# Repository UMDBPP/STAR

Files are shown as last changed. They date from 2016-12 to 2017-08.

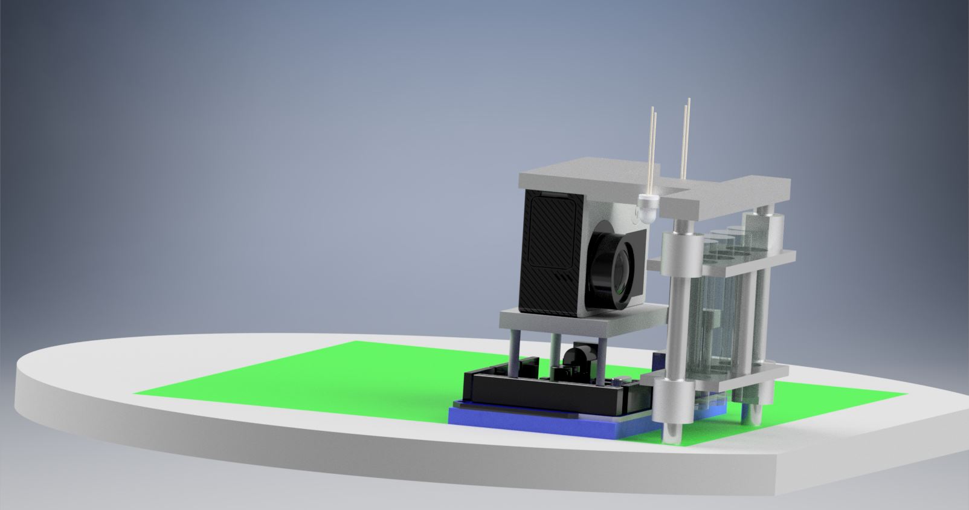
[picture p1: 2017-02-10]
CAD/Mechanical/Renderings and PDFs/Full payload assembly.jpg

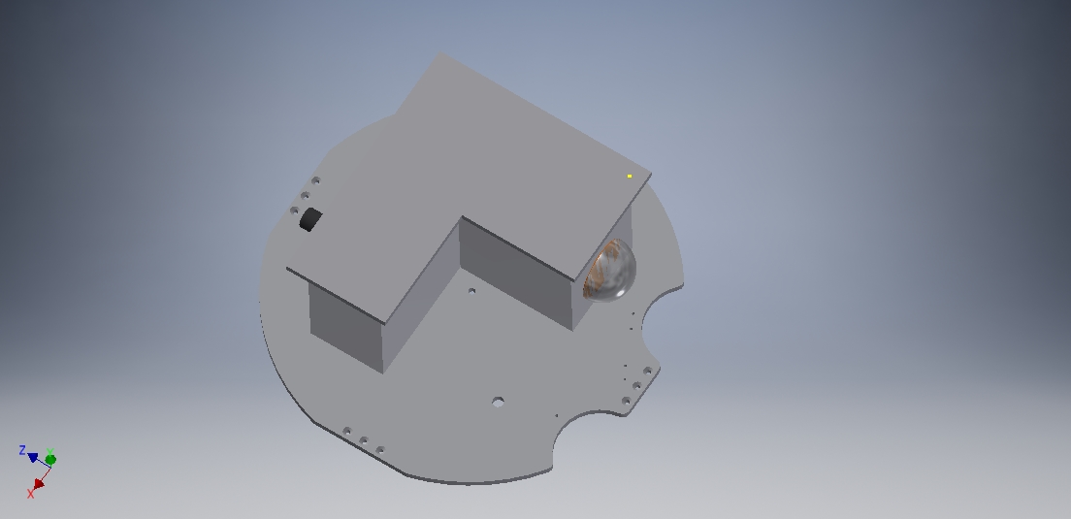
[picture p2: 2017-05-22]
CAD/Mechanical/CapTech/CADD/CADD/RSX Assembly/RSX Assembly.jpg

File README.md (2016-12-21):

# STAR
Sratification and Tribocharging Analysis of Regolith

## Purpose
This is a payload for the 2017 RockSatX project. It's purpose is to provide experimental data for validating a behavioral model proposed by Dr. Christine Hartzell.

The payload will:
* Observe stratification of varying bimodal grain size distribution under microgravity and external excitation
* Measure effect of tribocharging upon spherical non-conducting grains

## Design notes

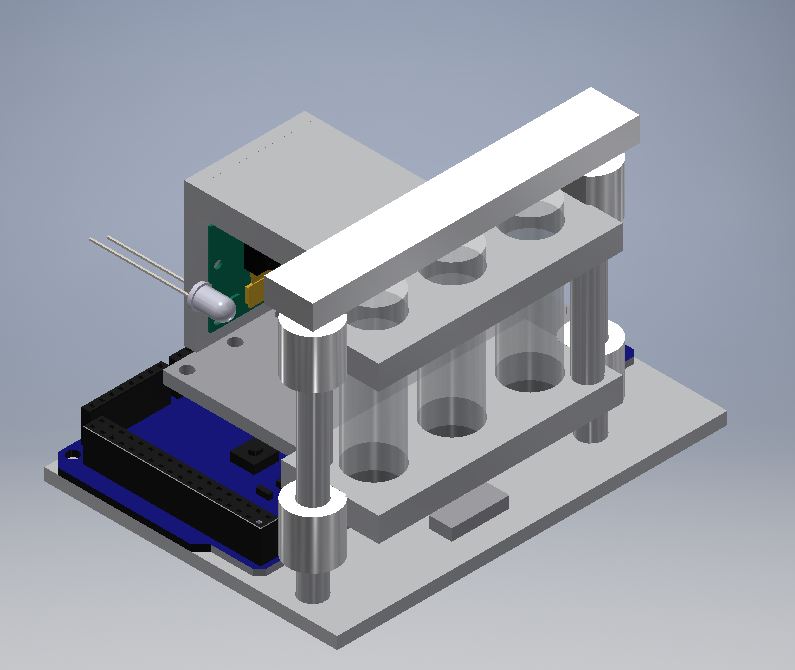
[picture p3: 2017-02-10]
CAD/Mechanical/Renderings and PDFs/Quick cad image.JPG

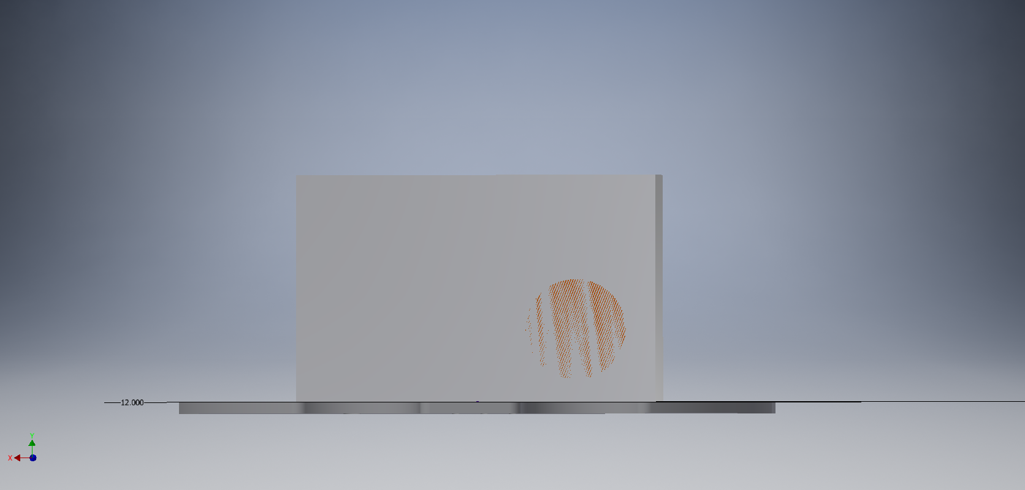
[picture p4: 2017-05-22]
CAD/Mechanical/CapTech/CADD/CADD/RSX structure separate walls/front.bmp

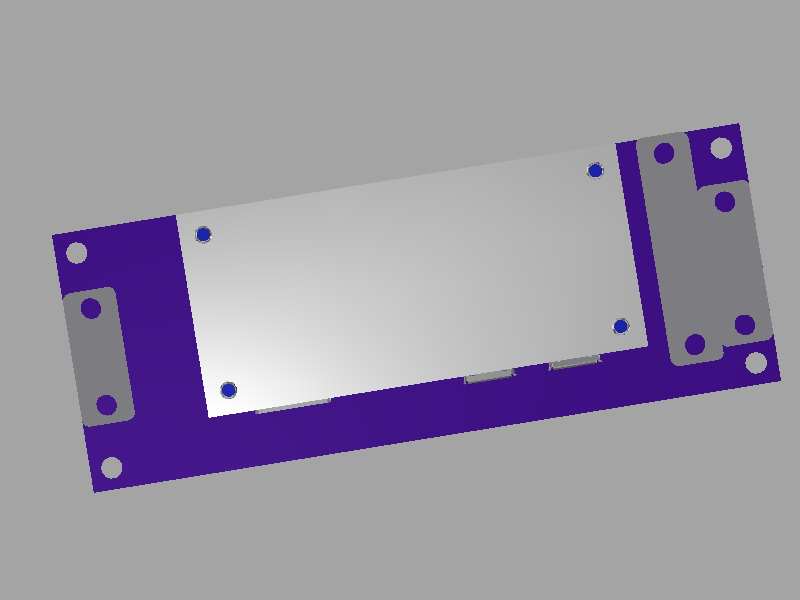
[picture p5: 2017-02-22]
CAD/Mechanical/Renderings and PDFs/STARduino + pi + connectors.png

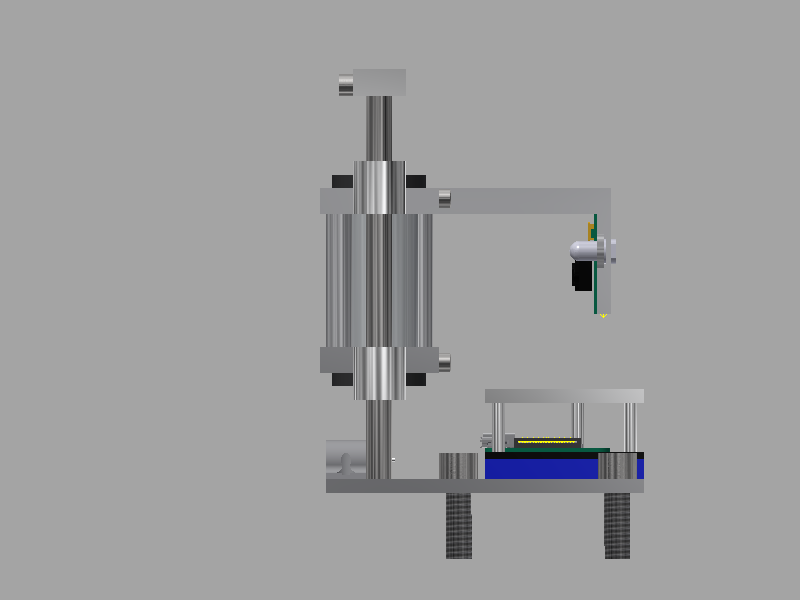
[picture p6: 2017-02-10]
CAD/Mechanical/Renderings and PDFs/motor config 2.png

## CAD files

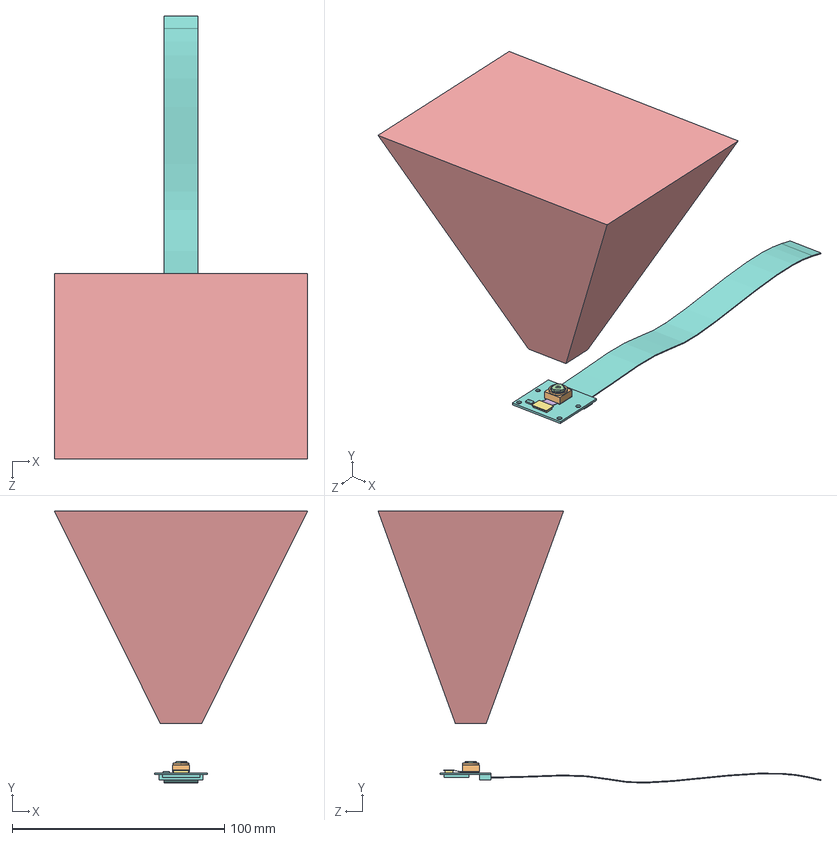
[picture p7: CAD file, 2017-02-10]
CAD/Mechanical/Full payload assembly/Subsystems/Pi Cam/Raspberry Pi Camera.STEP
119.2 x 128.0 x 208.5 mm
OVA5647
OVA5647_Housing
OVA5647_IR-Glas
OVA5647_Lens_FOV
OVA5647_Pigtail
RasPi_Camera_Board

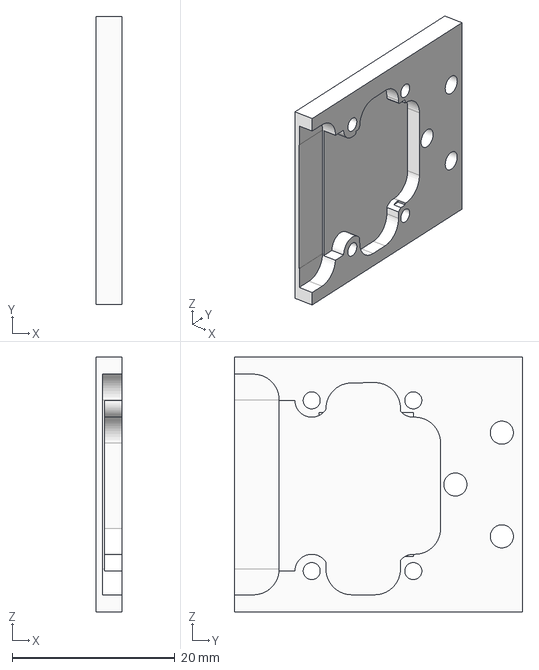
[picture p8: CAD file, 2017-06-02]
CAD/Mechanical/STEP Files/Pi cCam Mount.stp
3.17 x 35.4 x 31.4 mm

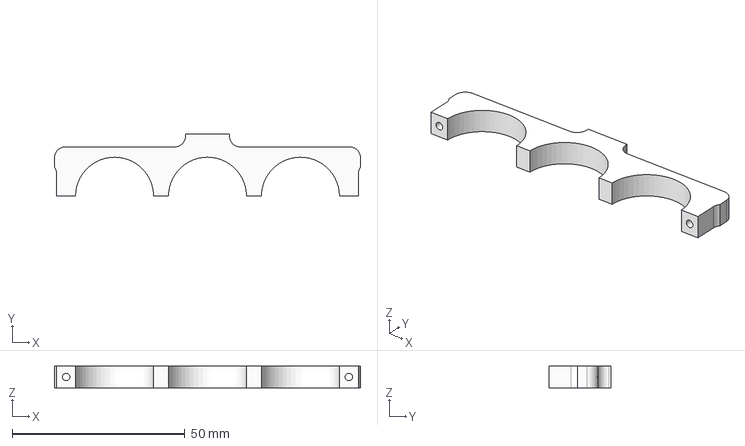
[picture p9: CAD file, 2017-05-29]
CAD/Mechanical/STEP Files/Tube Holder Halve 2.stp
88.6 x 18.1 x 6.35 mm

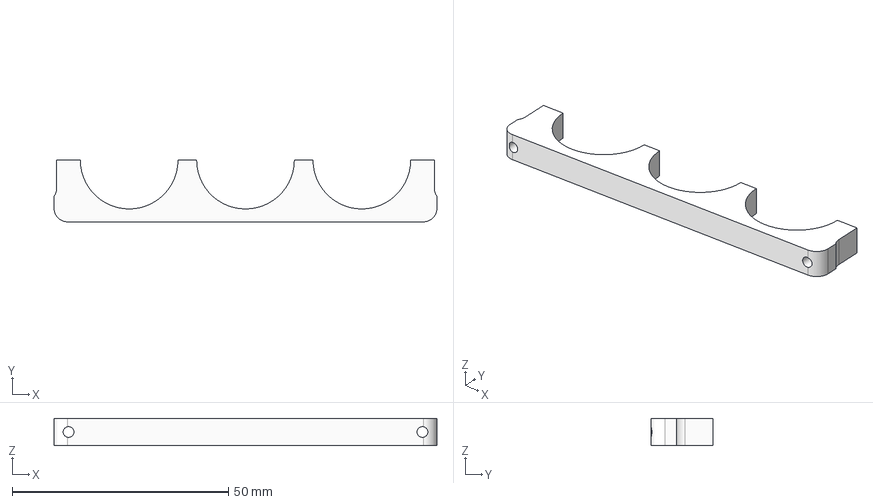
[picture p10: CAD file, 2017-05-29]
CAD/Mechanical/STEP Files/Tube Holder Halve 3.stp
88.6 x 14.3 x 6.35 mm

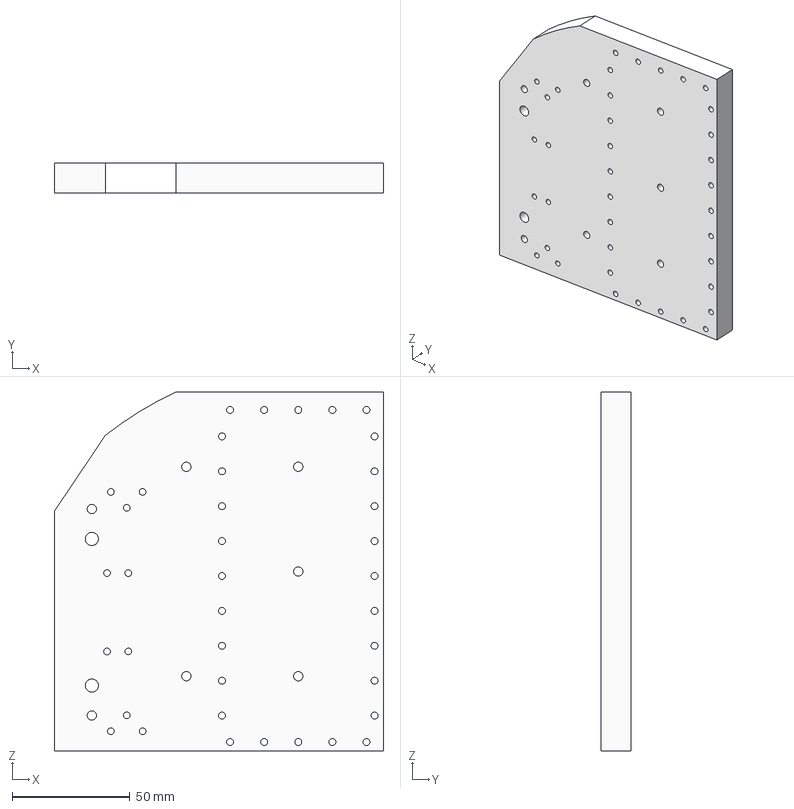
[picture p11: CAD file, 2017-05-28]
CAD/Mechanical/STEP Files/Base Plate Mk 2.stp
139.7 x 12.7 x 152.4 mm

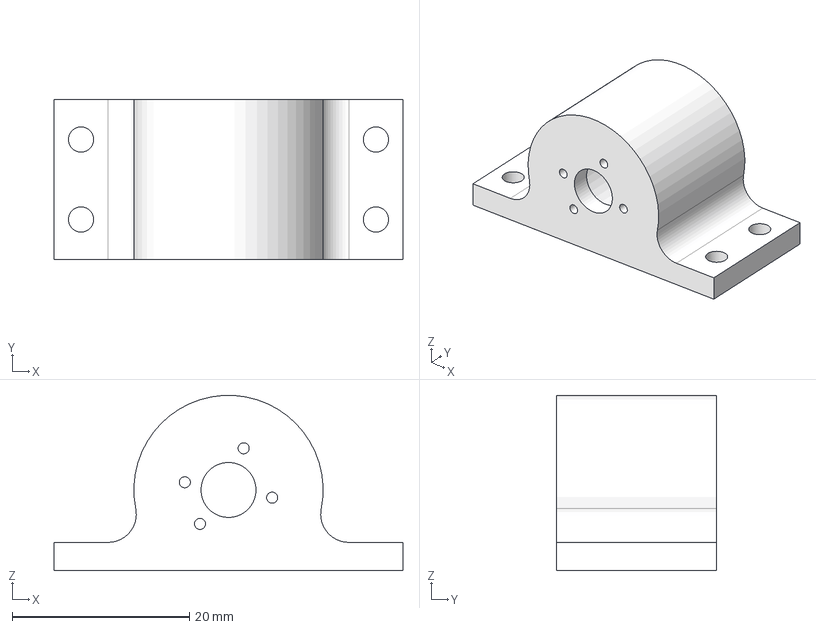
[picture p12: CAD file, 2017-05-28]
CAD/Mechanical/STEP Files/Motor Holder.stp
39.4 x 18.0 x 19.7 mm

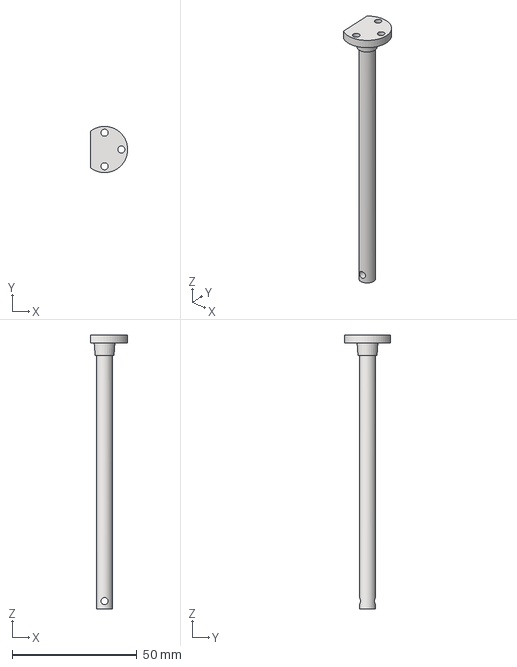
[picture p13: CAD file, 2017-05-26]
CAD/Mechanical/STEP Files/slide rod.stp
15.0 x 18.5 x 109.9 mm

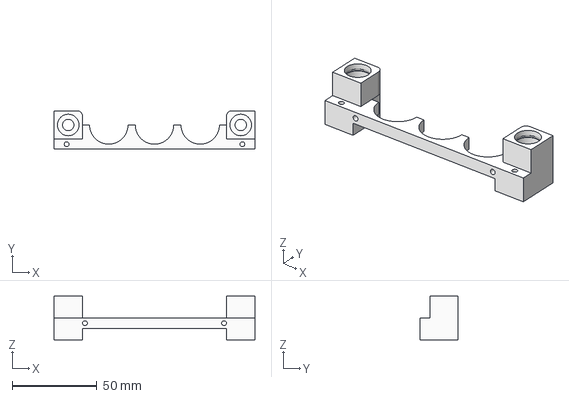
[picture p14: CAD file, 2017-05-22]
CAD/Mechanical/STEP Files/Tube Holder Halve.stp
118.4 x 22.7 x 25.6 mm

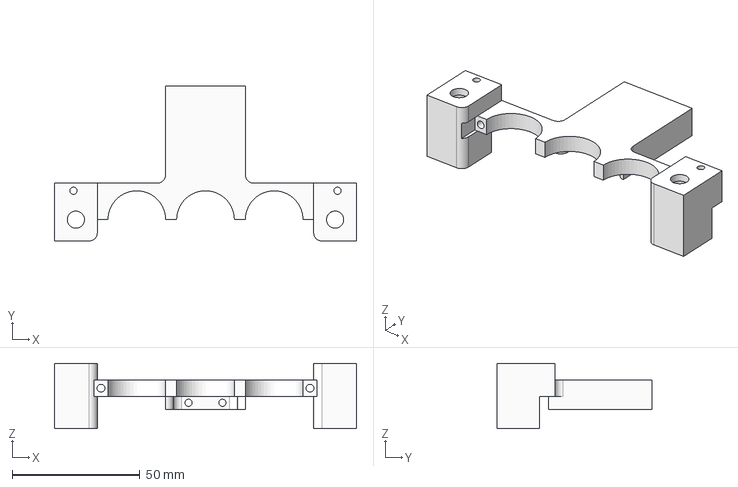
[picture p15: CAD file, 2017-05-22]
CAD/Mechanical/STEP Files/Tube Holder with camera attachment.stp
118.4 x 60.8 x 25.6 mm

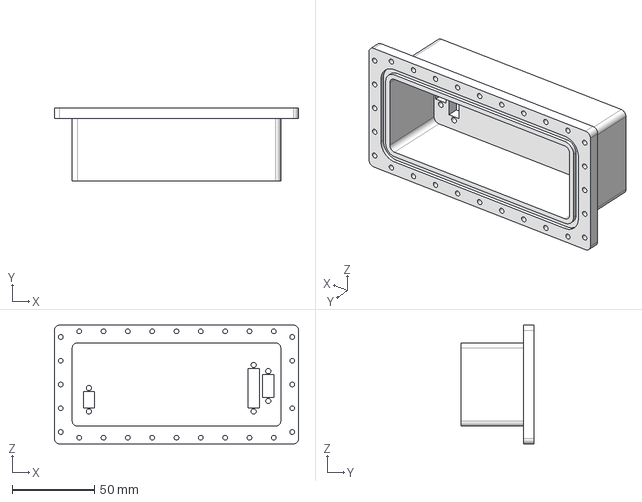
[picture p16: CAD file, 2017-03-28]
CAD/Mechanical/STEP Files/Electronics Box.stp
148.6 x 44.4 x 72.4 mm

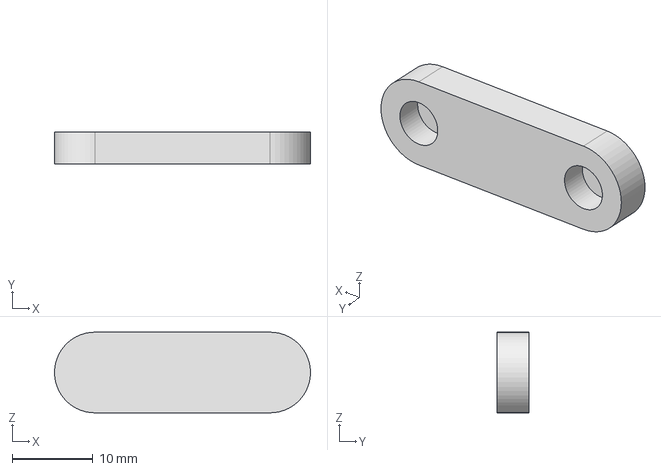
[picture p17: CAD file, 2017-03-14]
CAD/Mechanical/STEP Files/Linkage.stp
31.7 x 4.00 x 10.0 mm

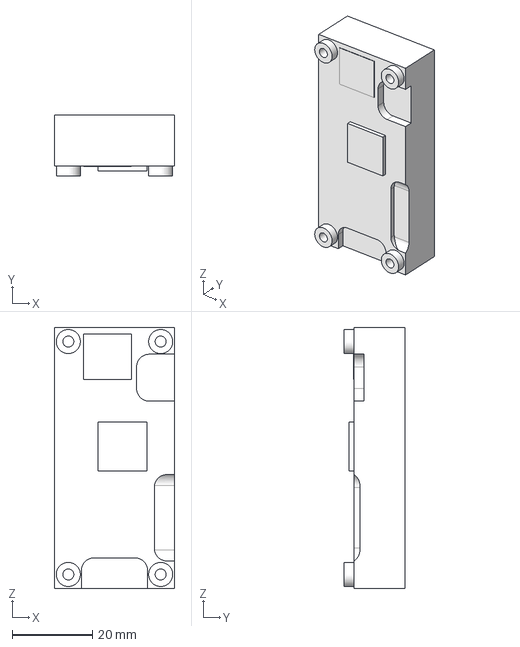
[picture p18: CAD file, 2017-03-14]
CAD/Mechanical/STEP Files/Heat Block for Pi.stp
30.0 x 15.1 x 65.0 mm

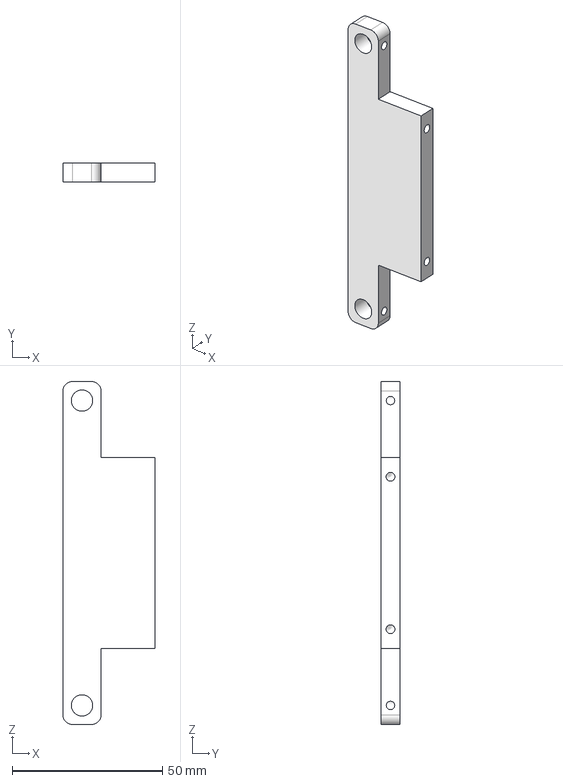
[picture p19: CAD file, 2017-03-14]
CAD/Mechanical/STEP Files/Slide rod connector.stp
30.7 x 6.35 x 114.3 mm

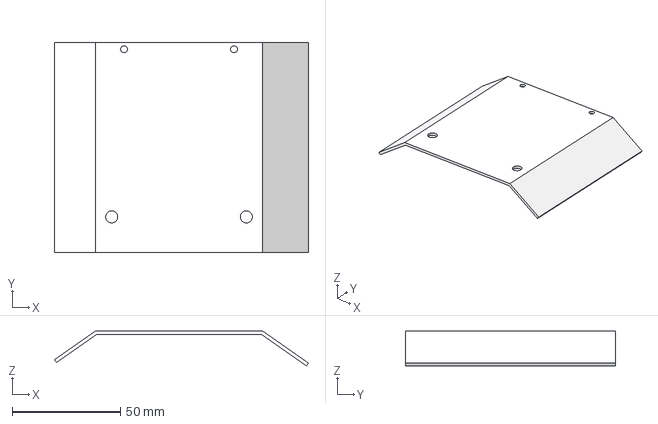
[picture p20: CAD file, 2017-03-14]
CAD/Mechanical/STEP Files/solar sheild.stp
117.4 x 97.2 x 16.2 mm

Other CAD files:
CAD/Mechanical/CapTech/CADD/CADD/RSX Assembly/RSX Assembly Lid.dwg
CAD/Mechanical/CapTech/CADD/CADD/RSX Assembly/RSX Assembly.dwg
CAD/Mechanical/91075A105_18-8 SS MALE-FEM THRDED HEX STANDOFF.SLDPRT
CAD/Mechanical/Full payload assembly/Subsystems/Fasteners/M2.5 16mm Socket Screw.STEP
CAD/Mechanical/1556A650_BRACKET.SLDPRT
CAD/Mechanical/94518A210_MIL SPEC FLAT-HEAD SOCKET CAP SCREW.ipt
CAD/Mechanical/98019A314_MIL SPEC. 300 SERIES SS FLAT WASHER.ipt
CAD/Mechanical/CAM/Camea_holder.f3d
CAD/Mechanical/CAM/Linkage.f3d
CAD/Mechanical/CAM/Pi_Heatsink.f3d
CAD/Mechanical/CAM/Slide_Rods.f3d
CAD/Mechanical/CAM/bottom_tube_holder.f3d
CAD/Mechanical/CAM/motor_holder.f3d
CAD/Mechanical/CAM/pi_holder.f3d
CAD/Mechanical/CAM/slide_connectors.f3d
CAD/Mechanical/CAM/test_tube_holder.f3d
CAD/Mechanical/CAM/top_tube_holder.f3d
CAD/Mechanical/CapTech/Antenna.ipt
CAD/Mechanical/CapTech/Bolt outline.iam
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

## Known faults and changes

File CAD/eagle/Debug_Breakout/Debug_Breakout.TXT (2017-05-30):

%
M48
M72
T01C0.0130
T02C0.0236
T03C0.0315
T04C0.0394
T05C0.0400
%
T01
X2700Y1650
X4300Y3650
X2700Y5700
X4550Y7850
X3150Y9650
X6150Y12150
X7200Y14150
X4650Y15650
X7150Y8200
X7950Y5750
X6250Y3250
X6300Y1750
T02
X8650Y5150
T03
X2713Y4634
X2713Y6666
X2713Y8634
X2713Y2666
T04
X1650Y2321
X1650Y4979
X1650Y6321
X1650Y8979
T05
X2150Y10650
X2150Y11650
X2150Y12650
X2150Y13650
X2150Y14650
X2150Y15650
X5650Y9650
X5650Y8650
X6150Y5150
X6150Y4150
X10650Y4400
X10650Y3400
X10650Y2400
X10650Y5400
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

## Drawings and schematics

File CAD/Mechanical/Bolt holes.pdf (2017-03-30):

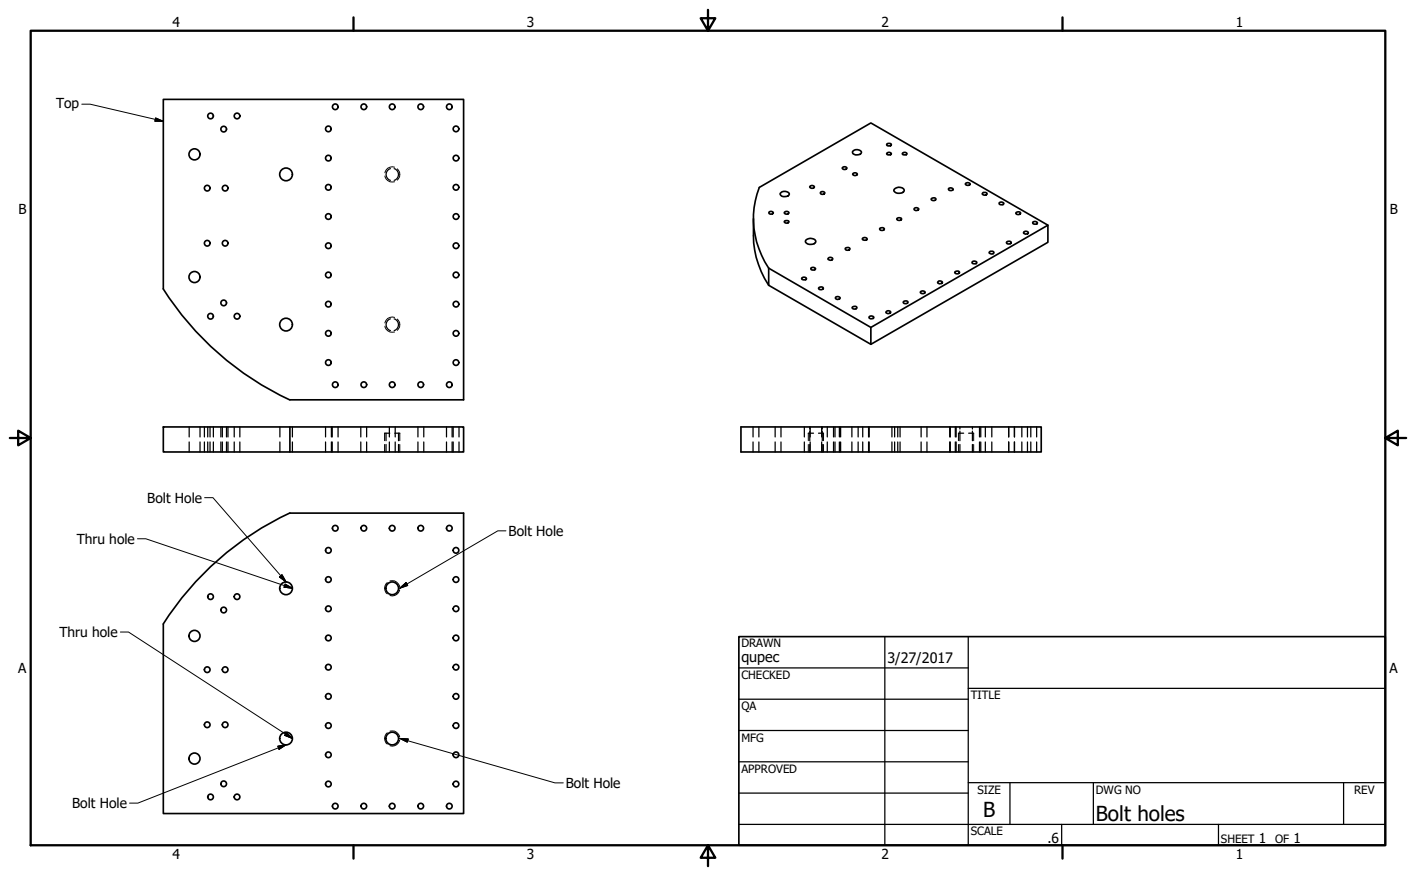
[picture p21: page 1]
SHEET 1 OF 1; DRAWN; CHECKED; MFG; APPROVED; qupec; DWG NO Bolt holes; TITLE; SIZE B; SCALE; REV; Top; Bolt Hole; Thru hole

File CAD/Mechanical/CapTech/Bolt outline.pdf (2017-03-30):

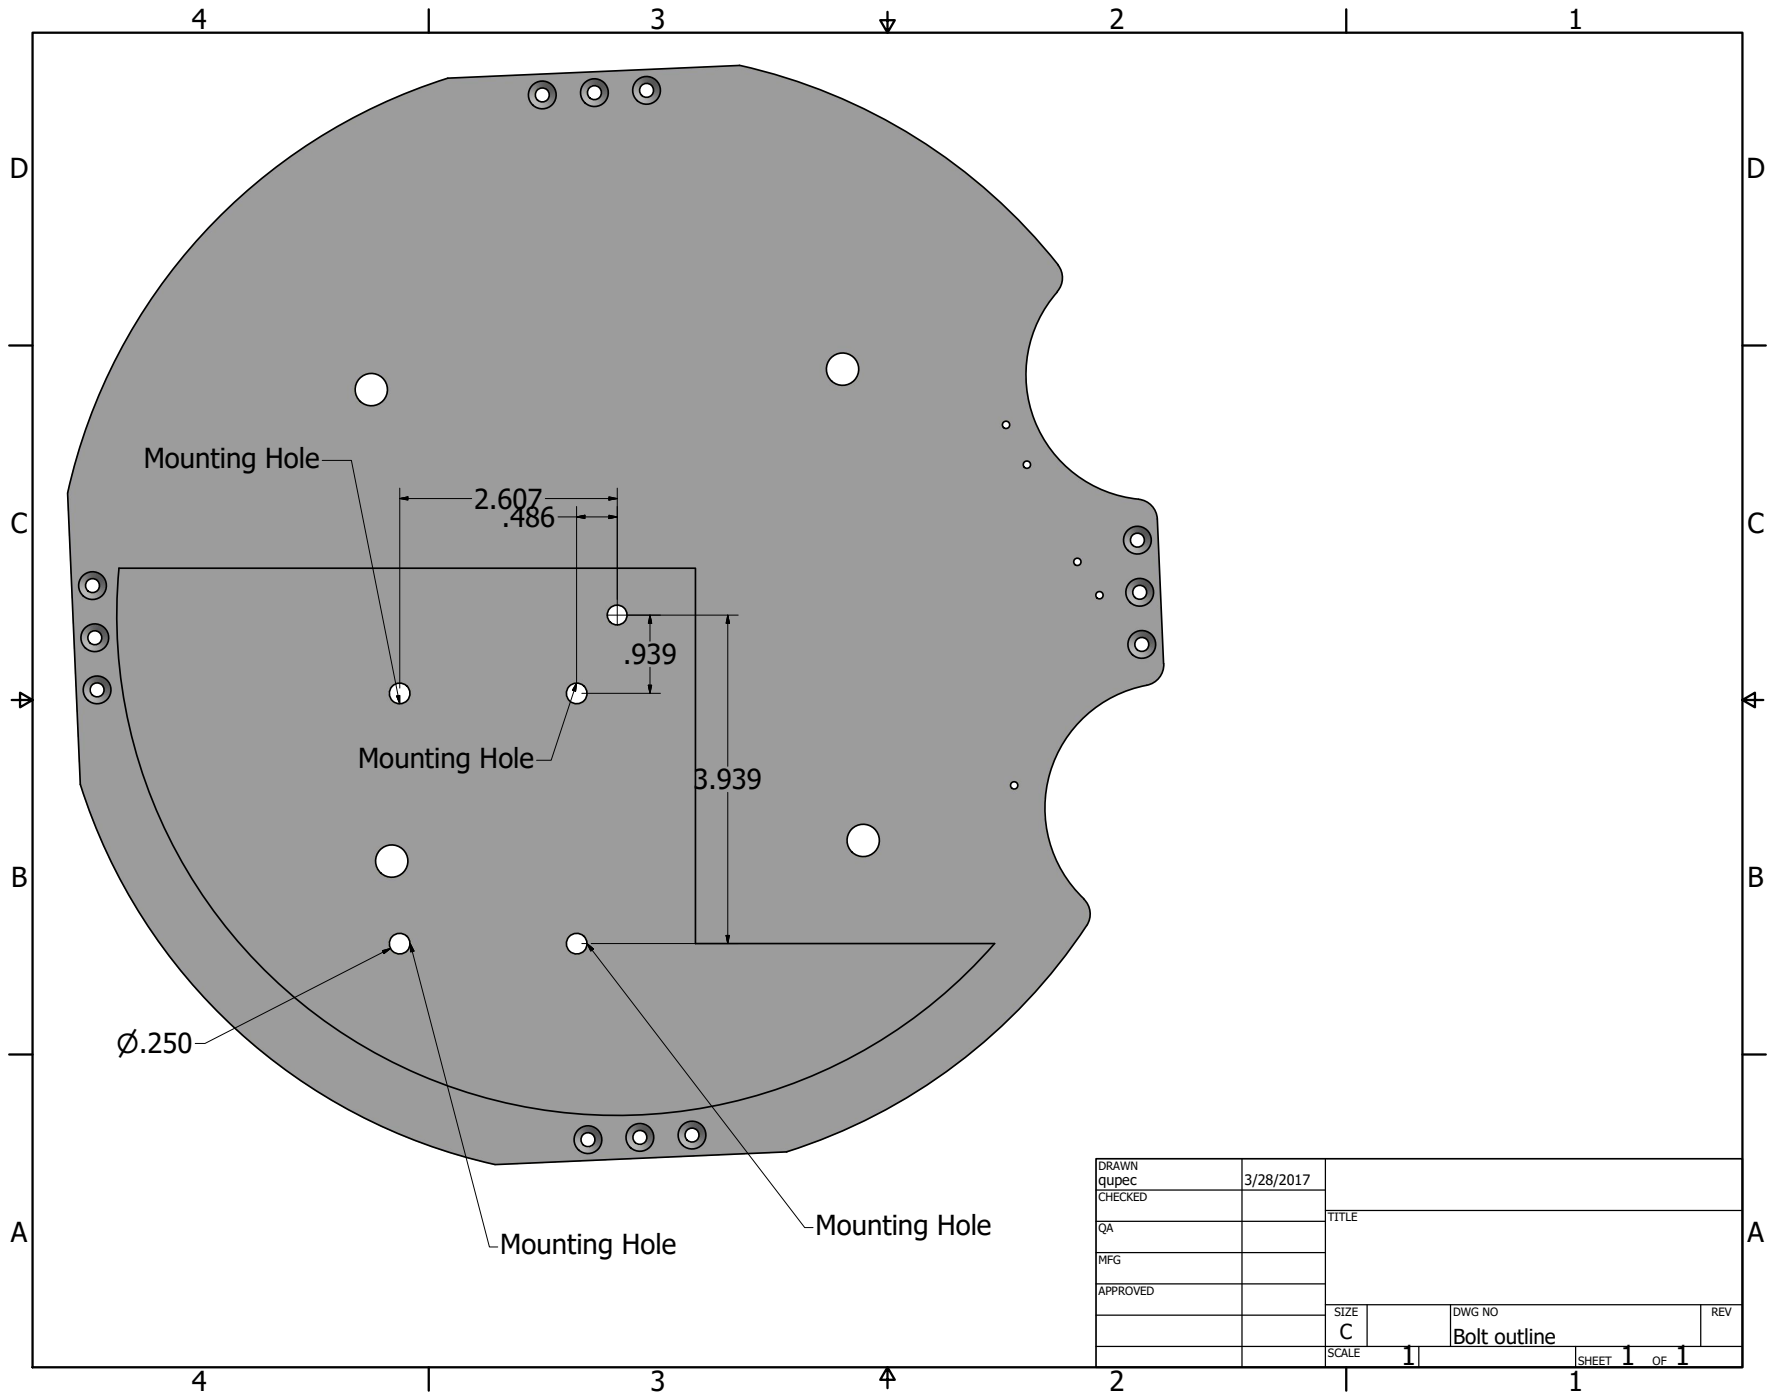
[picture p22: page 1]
SHEET 1 OF 1; DRAWN; CHECKED; MFG; APPROVED; qupec; DWG NO Bolt outline; TITLE; SIZE C; SCALE; REV; Mounting Hole

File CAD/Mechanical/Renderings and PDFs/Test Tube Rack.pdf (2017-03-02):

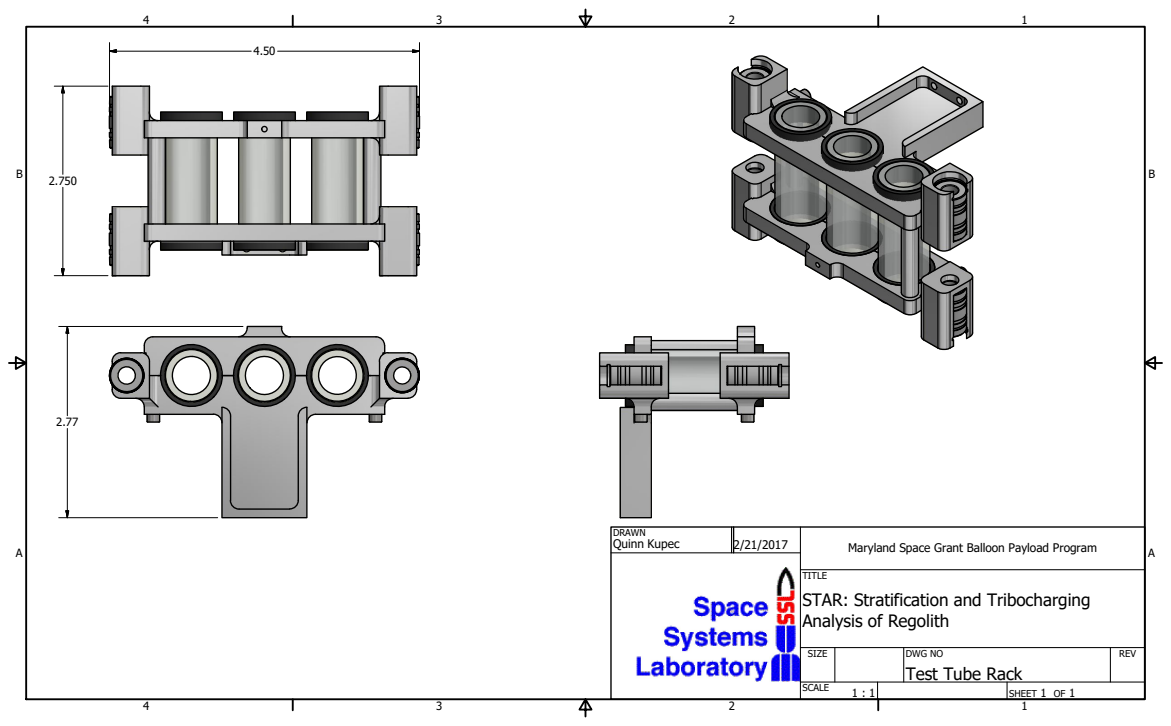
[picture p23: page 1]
SHEET 1 OF 1; DRAWN; Quinn Kupec; SIZE; SCALE; REV

Maryland Space Grant Balloon Payload Program

TITLE
STAR: Stratification and Tribocharging
Analysis of Regolith

DWG NO
Test Tube Rack

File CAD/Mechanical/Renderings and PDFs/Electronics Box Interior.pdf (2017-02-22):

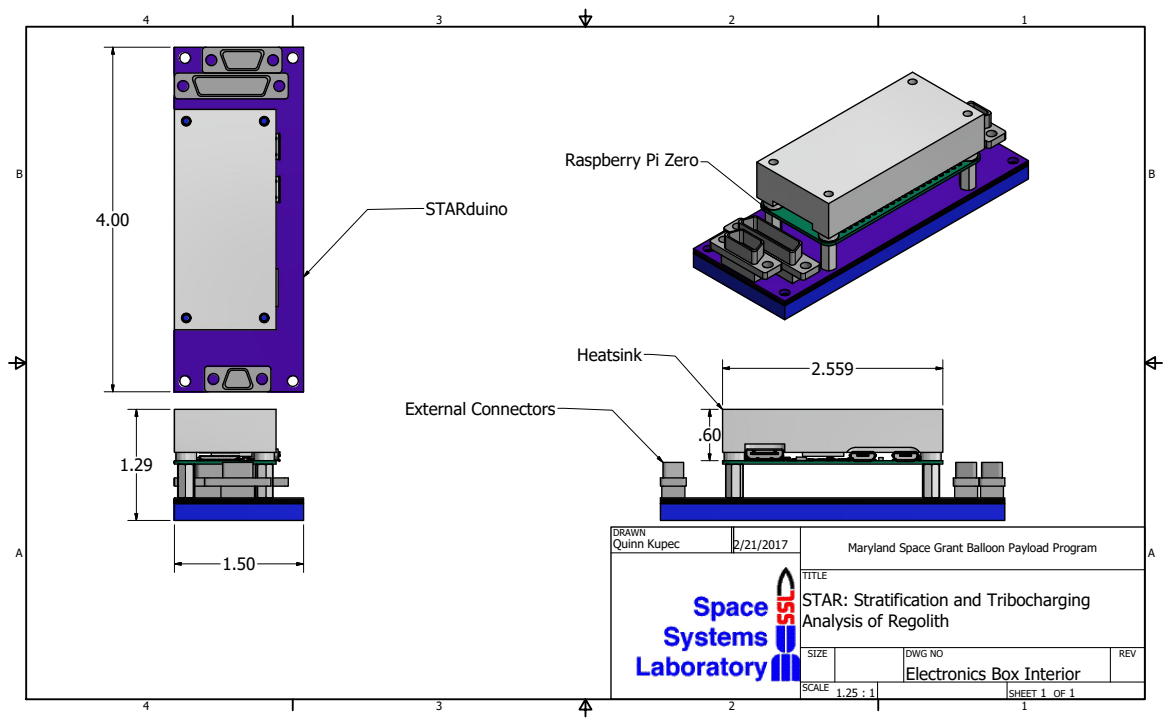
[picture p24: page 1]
SHEET 1 OF 1; DRAWN; Quinn Kupec; SIZE; SCALE; REV; Heatsink; STARduino; External Connectors

Raspberry Pi Zero

Maryland Space Grant Balloon Payload Program

TITLE
STAR: Stratification and Tribocharging
Analysis of Regolith

DWG NO
Electronics Box Interior

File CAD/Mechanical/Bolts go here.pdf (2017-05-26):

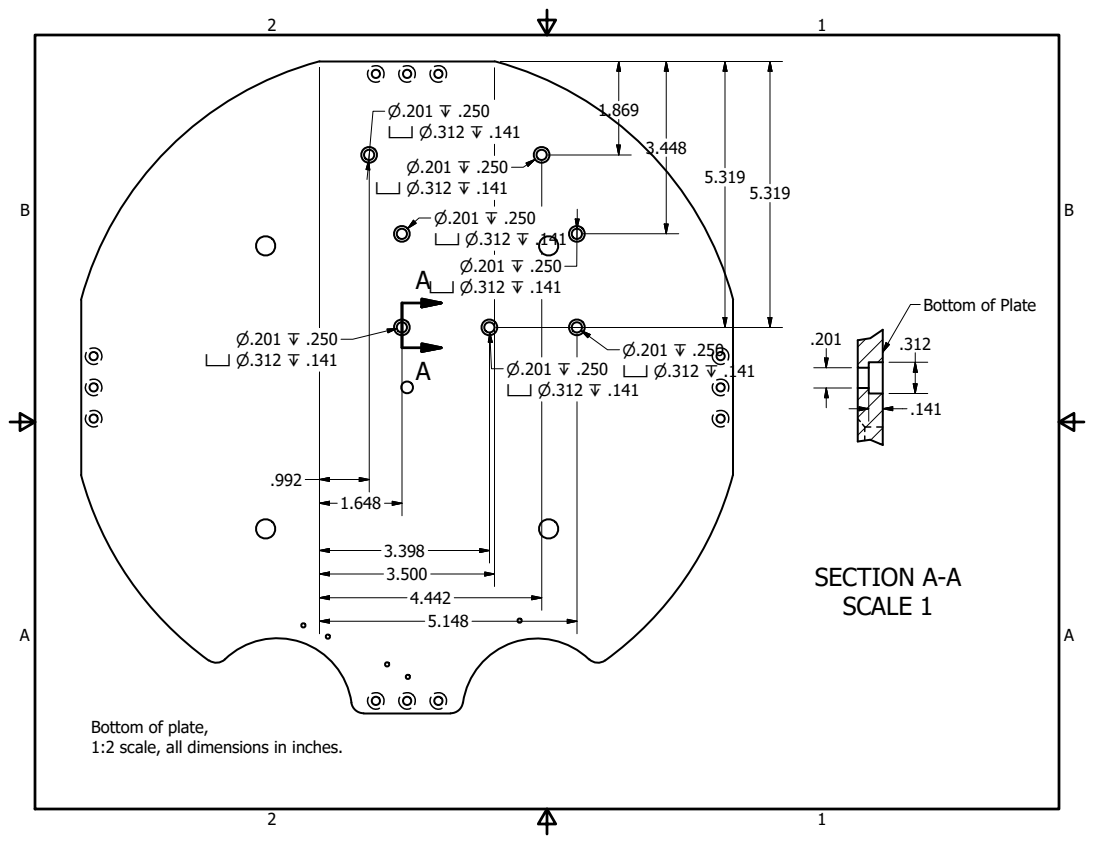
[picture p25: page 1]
SECTION A-A SCALE 1

Bottom of Plate

Bottom of plate,
1:2 scale, all dimensions in inches.

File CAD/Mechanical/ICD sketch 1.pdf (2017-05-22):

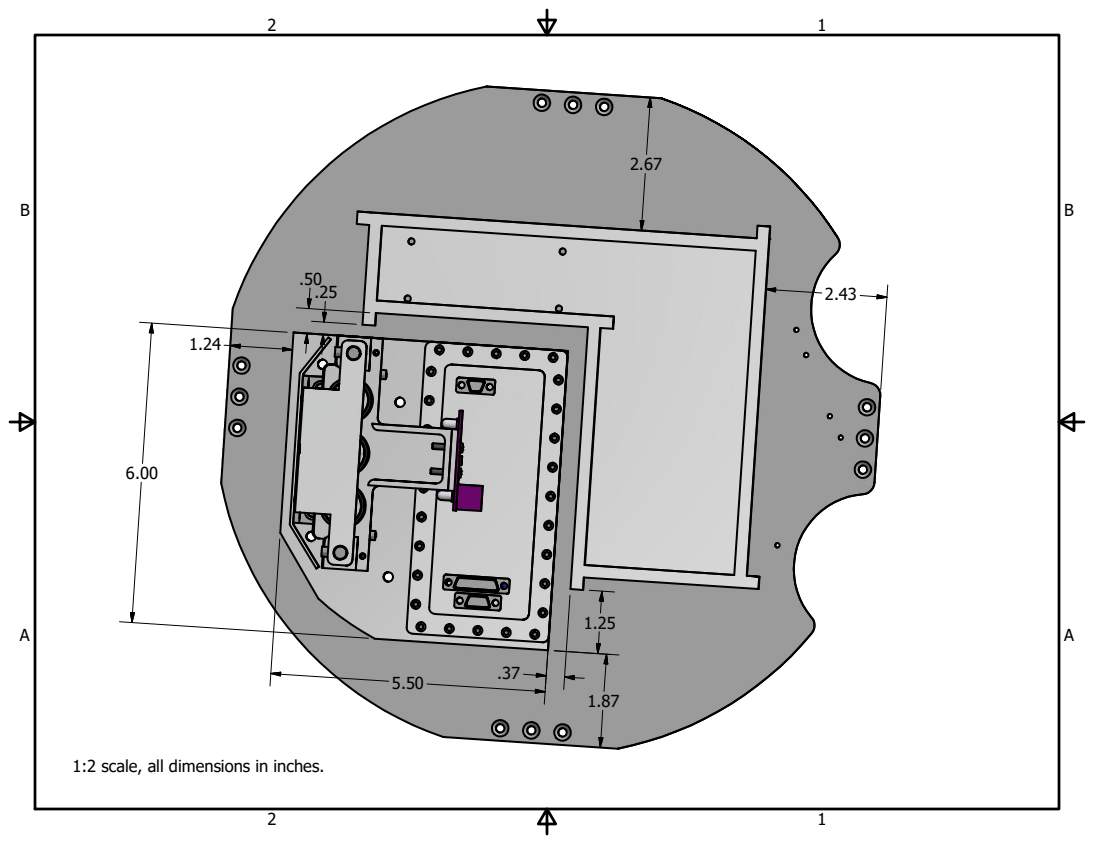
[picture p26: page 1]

1:2 scale, all dimensions in inches.

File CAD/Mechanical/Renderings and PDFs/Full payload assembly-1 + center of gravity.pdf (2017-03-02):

1

2

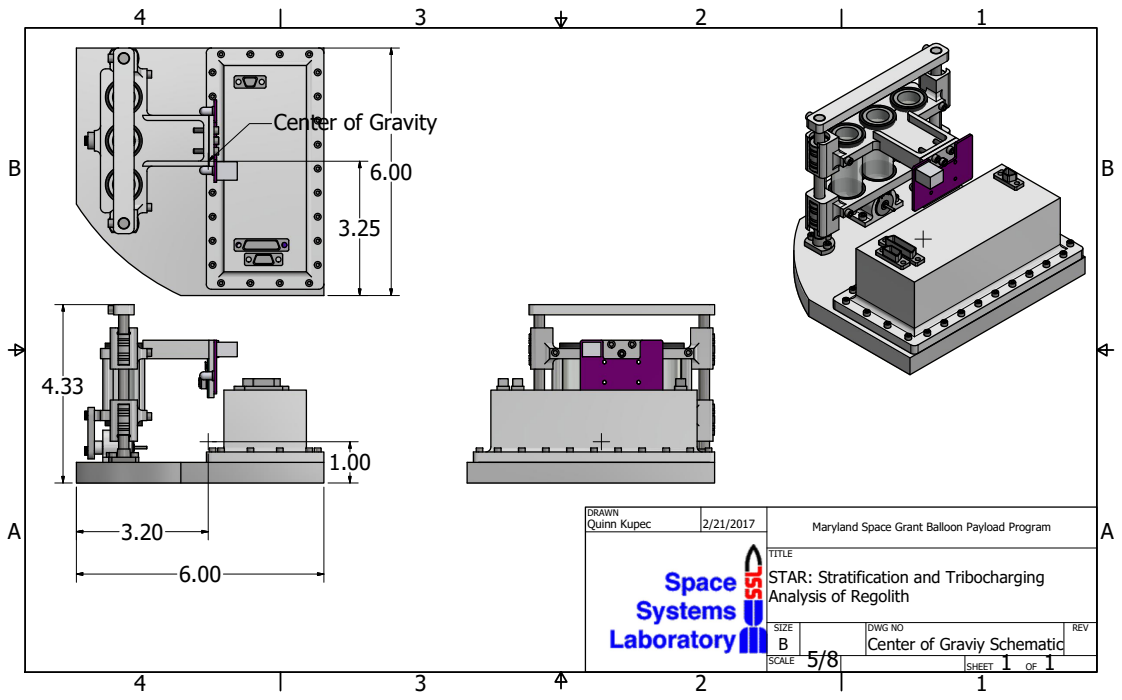
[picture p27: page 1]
SHEET 1 OF 1; DRAWN; Quinn Kupec; SIZE B; SCALE; REV

Center of Gravity

Maryland Space Grant Balloon Payload Program

TITLE
STAR: Stratification and Tribocharging
Analysis of Regolith

DWG NO
Center of Graviy Schematic

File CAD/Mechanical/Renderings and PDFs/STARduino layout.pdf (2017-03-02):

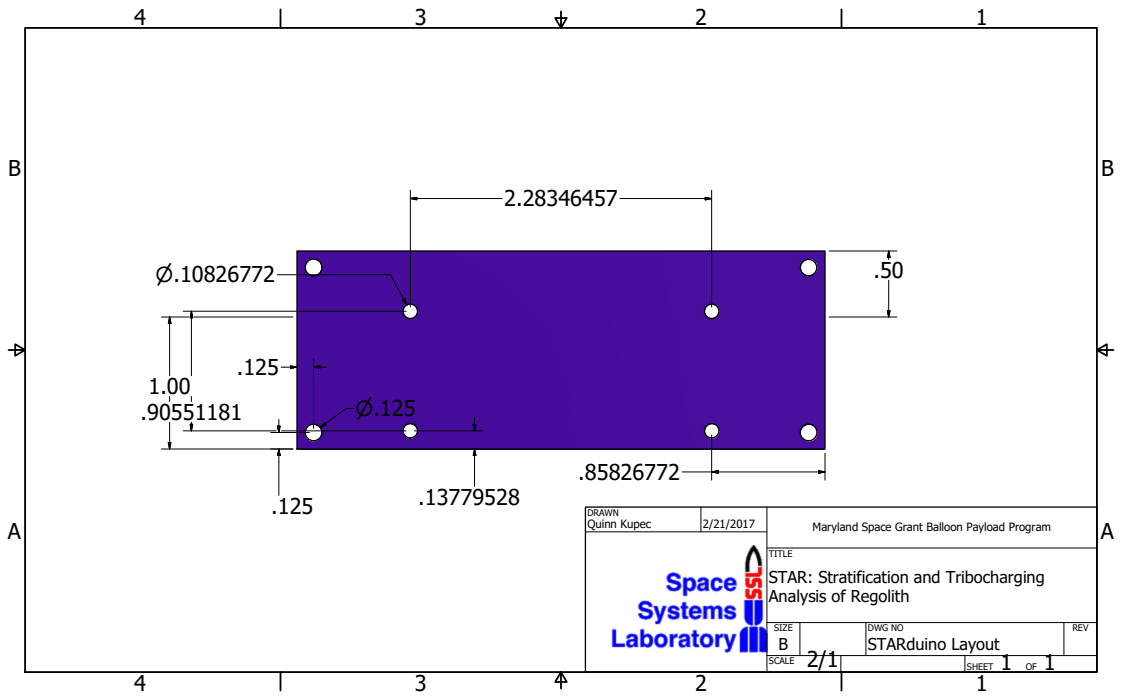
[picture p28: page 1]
SHEET 1 OF 1; DRAWN; Quinn Kupec; DWG NO STARduino Layout; SIZE B; SCALE; REV

Maryland Space Grant Balloon Payload Program

TITLE
STAR: Stratification and Tribocharging
Analysis of Regolith

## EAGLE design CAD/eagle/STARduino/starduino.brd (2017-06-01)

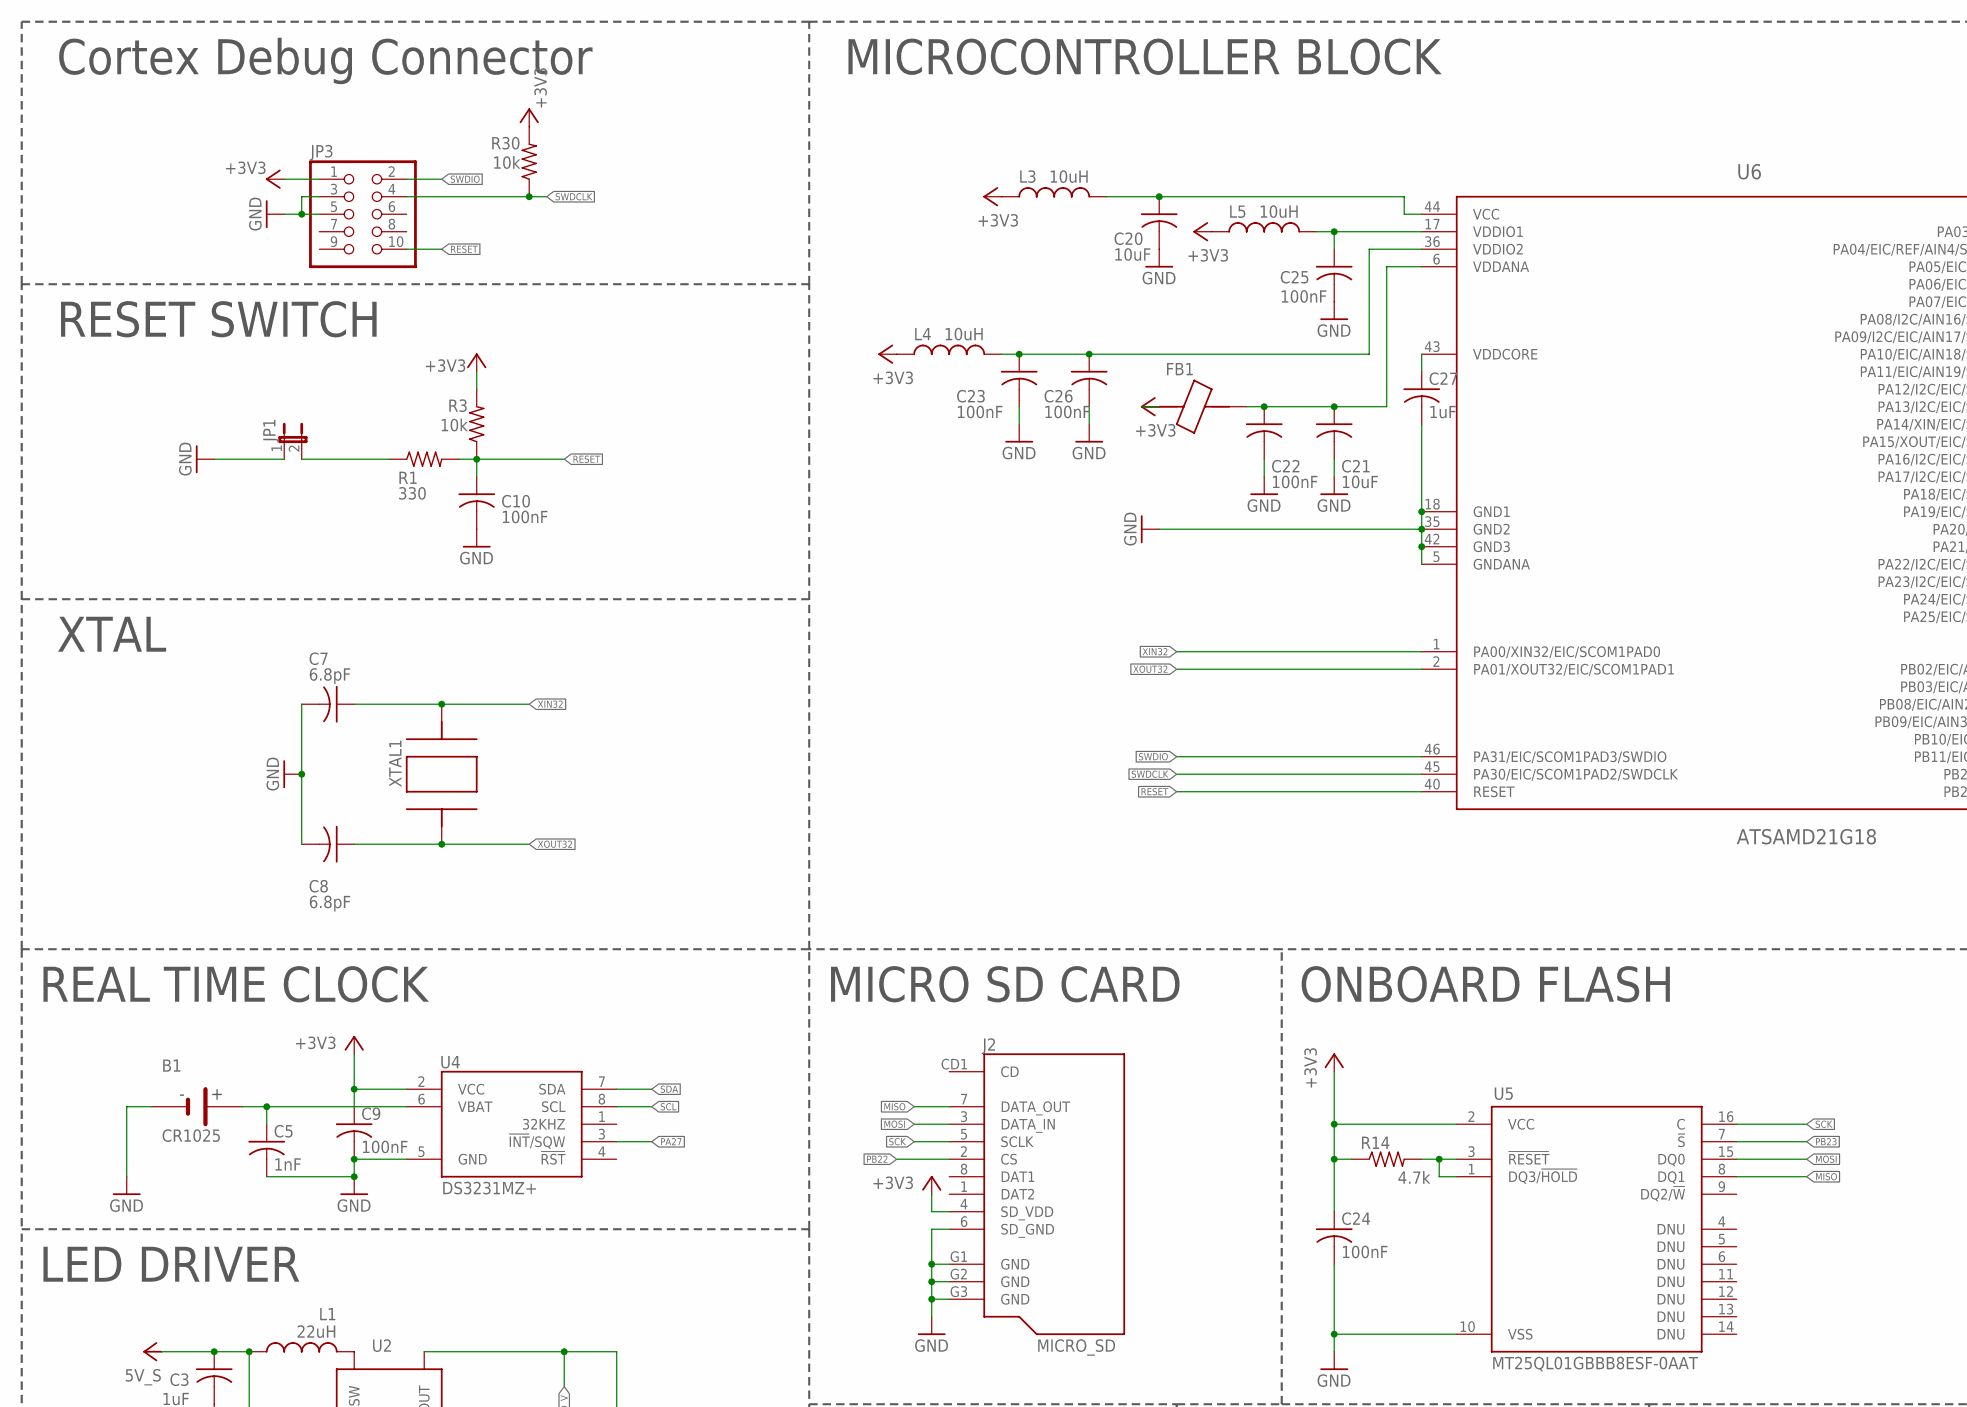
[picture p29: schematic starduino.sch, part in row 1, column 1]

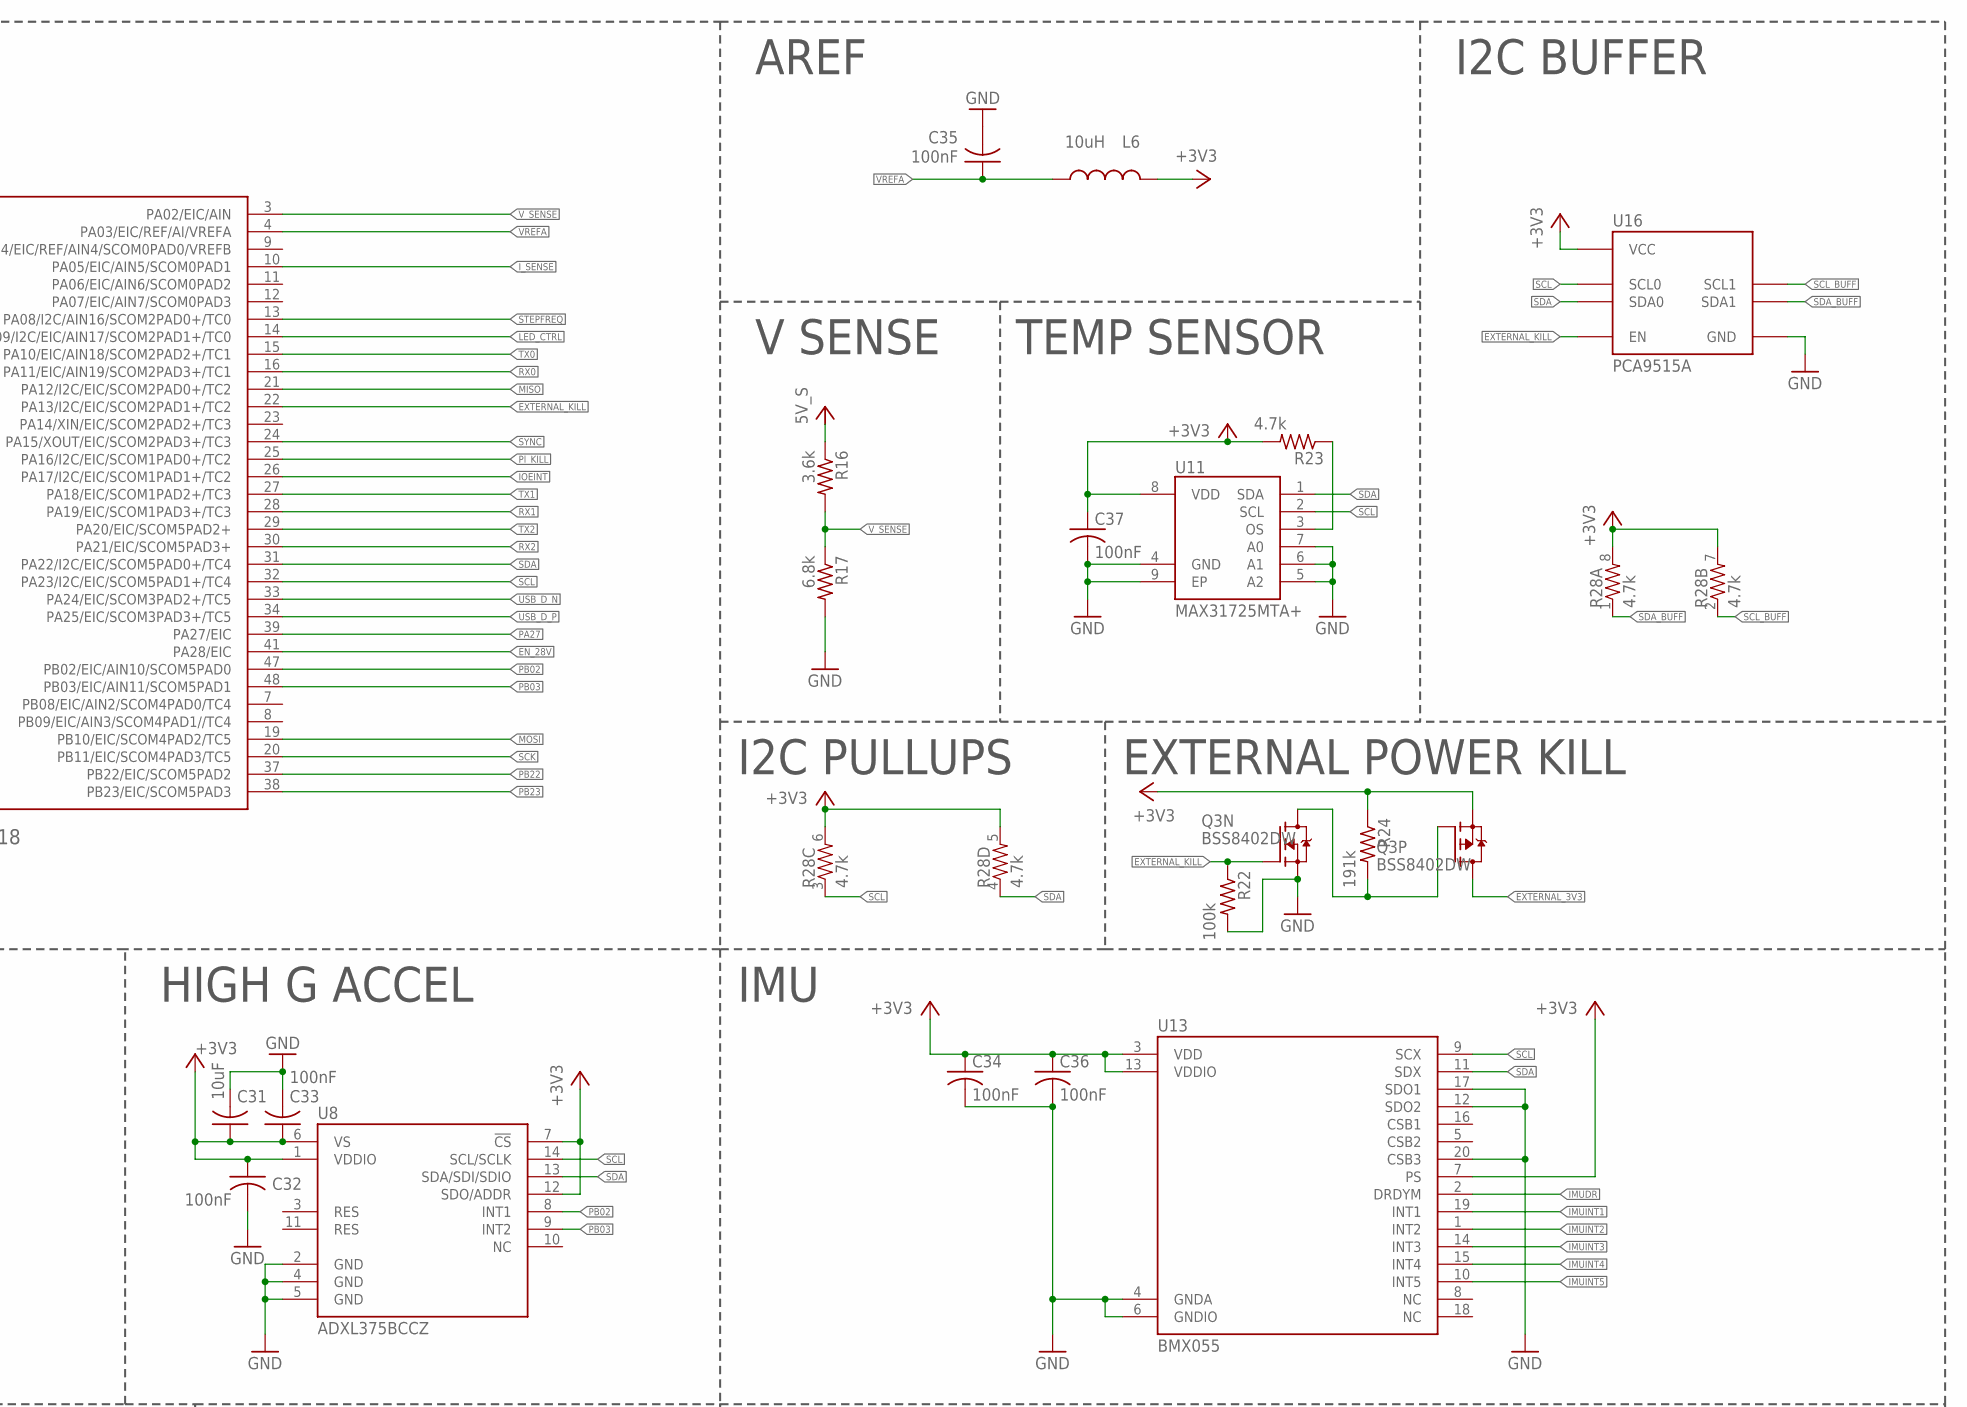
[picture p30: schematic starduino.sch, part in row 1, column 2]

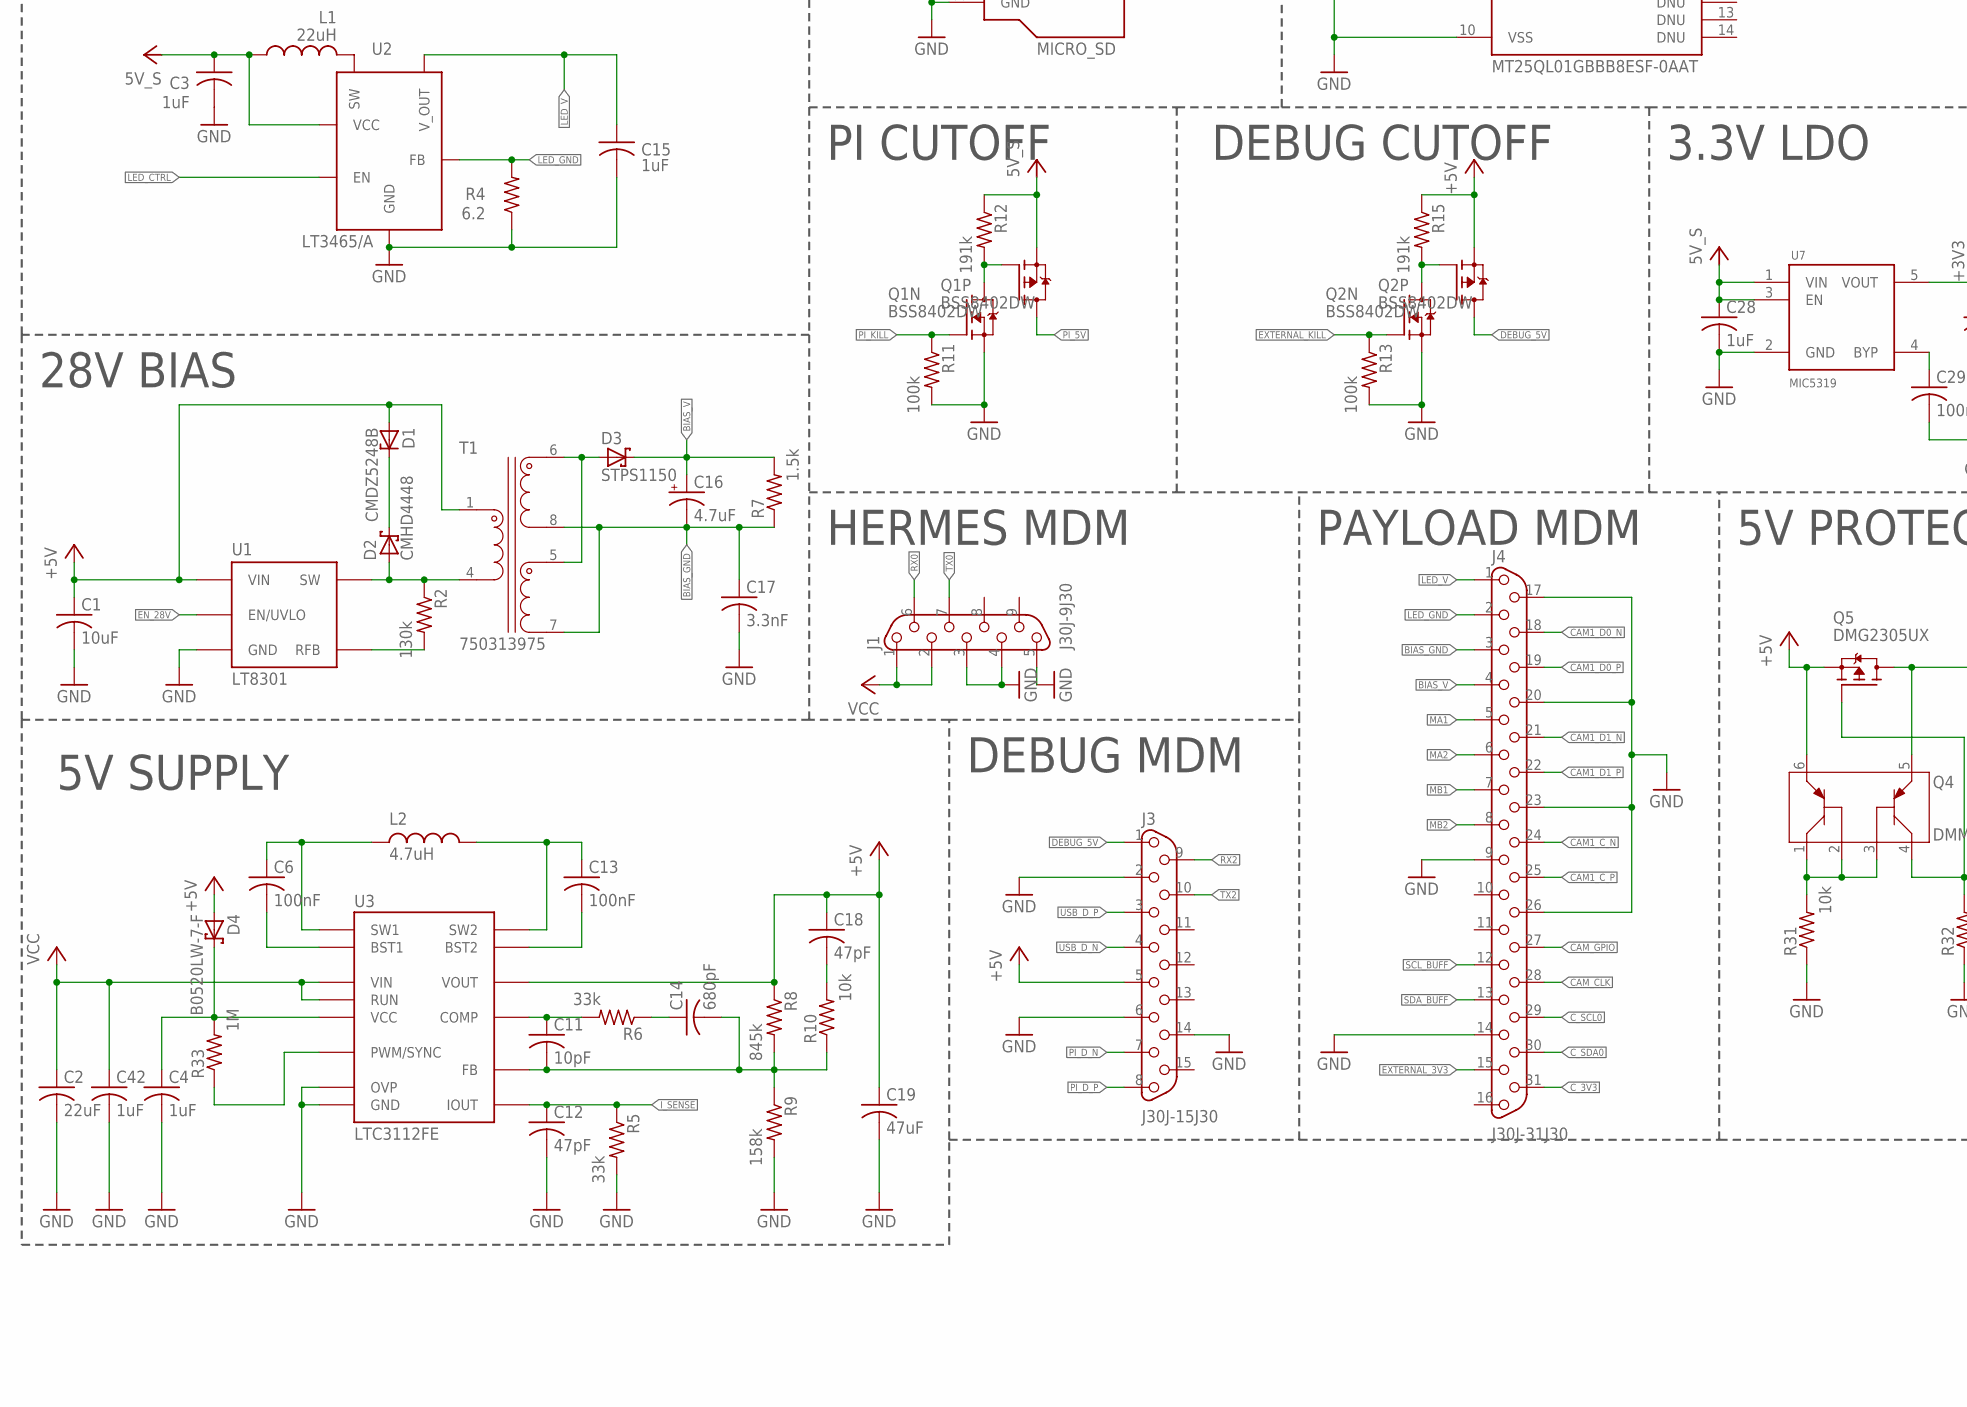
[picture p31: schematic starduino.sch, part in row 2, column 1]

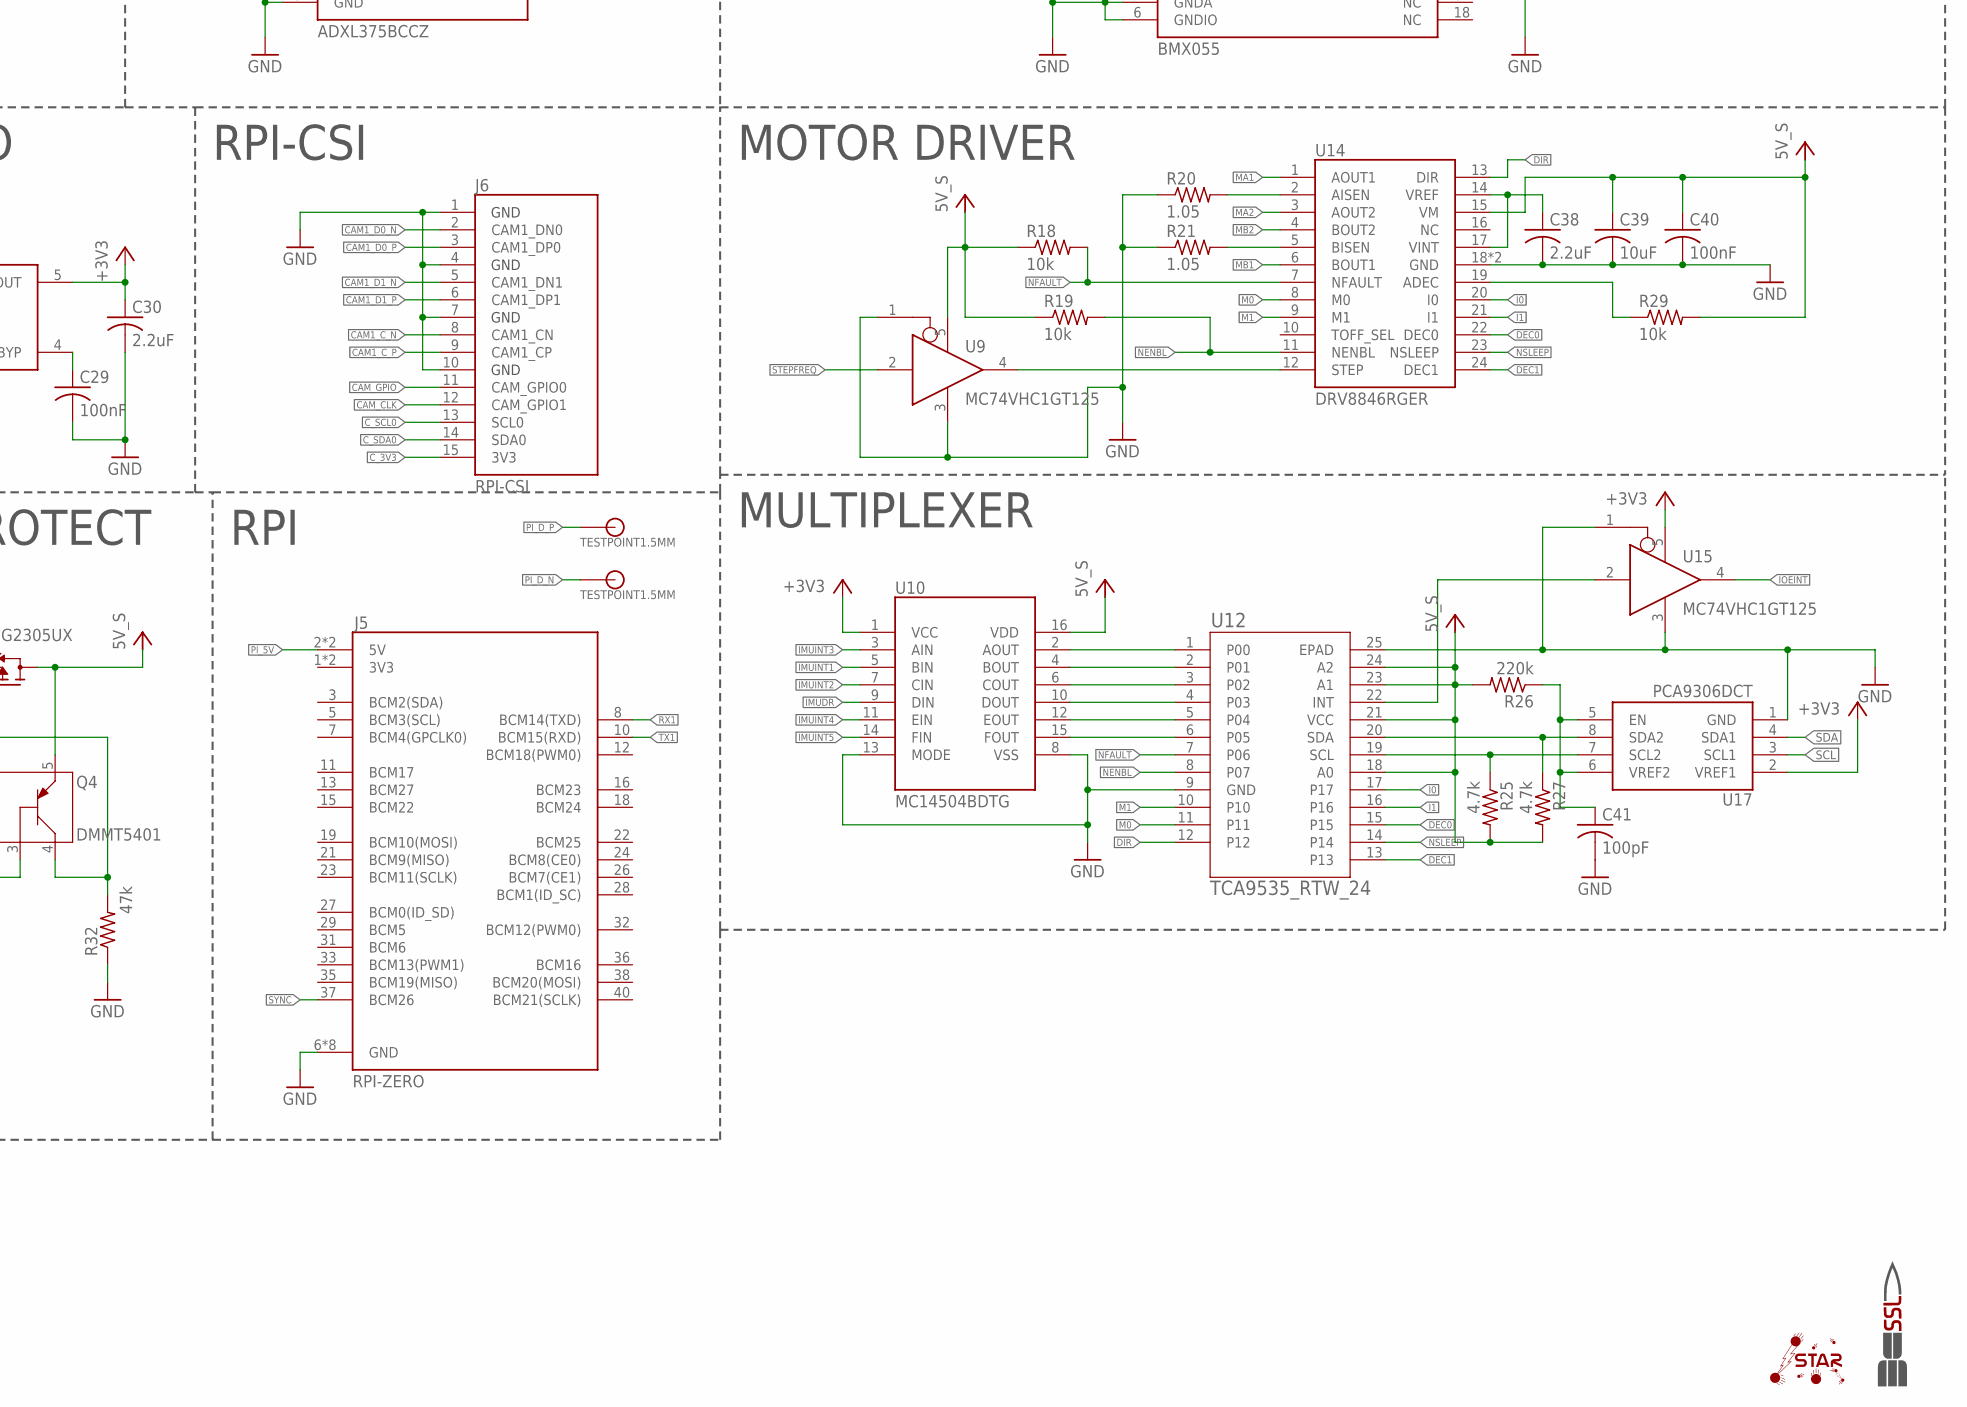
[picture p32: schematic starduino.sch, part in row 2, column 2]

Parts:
B1: CR1025
C1: 10uF; C1206
C2: 22uF; C1206
C3, C4, C15, C27, C28, C42: 1uF; C0603
C5: 1nF; C0603
C6, C9, C10, C13, C22, C23, C24, C25, C26, C29, C32, C33, C34, C35, C36, C37, C40: 100nF; C0603
C7, C8: 6.8pF; C0603
C11: 10pF; C0603
C12, C18: 47pF; C0603
C14: 680pF; C0603
C16: 4.7uF; KEMET_B
C17: 3.3nF; C1206
C19: 47uF; C1210
C20, C21, C31, C39: 10uF; C0603
C30, C38: 2.2uF; C0603
C41: 100pF; C0603
D1: CMDZ5248B; SOD323-W
D2: CMHD4448; SOD123
D3: STPS1150; SMA
D4: B0520LW-7-F; SOD123
FB1: BLM18KG221BH1D; 0603
J1: J30J-9J30; ZKN-9-J30
J2: MICRO_SD; MICROSD_PUSH_PUSH_AMPHENOL
J3: J30J-15J30; ZKN-15-J30
J4: J30J-31J30; ZKN-31-J30
J5: RPI-ZERO; 2X20-OFFSET
J6: RPI-CSI; 1-1734248-5
JP1: JUMPER-2PTH; 1X02
JP3: PINHD-2X5; 2X5/90-50MIL
L1: 22uH; VLF504012MT(TDK)
L2: 4.7uH; SRP5030
L3, L4, L5, L6: 10uH; 0603
Q1, Q2, Q3: BSS8402DW; SC70
Q4: DMMT5401; SOT-26
Q5: DMG2305UX; SOT23
R1: 330; R0603
R2: 130k; R0603
R3, R10, R18, R19, R29, R30, R31: 10k; R0603
R4: 6.2; R0603
R5, R6: 33k; R0603
R7: 1.5k; R1206
R8: 845k; R0603
R9: 158k; R0603
R11, R13, R22: 100k; R0603
R12, R15, R24: 191k; R0603
R14, R23, R25, R27: 4.7k; R0603
R16: 3.6k; R0603
R17: 6.8k; R0603
R20, R21: 1.05; R0603
R26: 220k; R0603
R28: 4.7k; 0603-ARV
R32: 47k; R0603
R33: 1M; R0603
T1: 750313975; 750313972
TP1, TP2: TESTPOINT1.5MM; TP-1.5MM
U1: LT8301; SOT23-5L
U2: LT3465/A; SOT23-6
U3: LTC3112FE; TSSOP20
U4: DS3231MZ+; SOIC-8
U5: MT25QL01GBBB8ESF-0AAT; SOP2-16
U6: ATSAMD21G18; 48-TQFP
U7: MIC5319; SOT23-5L
U8: ADXL375BCCZ; LGA-14
U9, U15: MC74VHC1GT125; SC-70-5
U10: MC14504BDTG; TSSOP16
U11: MAX31725MTA+; DFN-8
U12: TCA9535_RTW_24; RTW24_2P45X2P45
U13: BMX055; LGA-20
U14: DRV8846RGER; VQFN6
U16: PCA9515A; TSSOP8
U17: PCA9306DCT; SSOP8
U$1: STAR; STAR_.3IN
U$2: SSL.3IN_SILK; SSL_SILK_.3IN
XTAL1: ABS07AIG-32.768KHZ-1-T; 2-SMD

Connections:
5V_S: C3.1, C28.1, C39.1, C40.1, L1.P$1 (1), Q1.4 (S), Q4.5 (E2), Q5.3 (D), R12.1, R16.1, R18.1, R19.1, R25.2, R26.2, R27.2, R29.2, U2.5 (VCC), U7.1 (VIN), U7.3 (EN), U9.5 (VIN), U10.16 (VDD), U12.18 (A0), U12.21 (VCC), U12.23 (A1), U12.24 (A2), U14.15 (VM)
+3V3: C9.1, C24.1, C30.1, C31.1, C32.1, C33.1, C34.1, C36.1, C37.1, FB1.1, J2.4 (SD_VDD), JP3.1, L3.1, L4.1, L5.1, L6.2, Q3.4 (S), R3.2, R14.1, R23.2, R24.1, R28.5 (2), R28.6 (2), R28.7 (2), R28.8 (2), R30.2, U4.2 (VCC), U5.2 (VCC), U7.5 (VOUT), U8.1 (VDDIO), U8.6 (VS), U8.7 (!CS!), U8.12 (SDO/ADDR), U10.1 (VCC), U11.8 (VDD), U13.3 (VDD), U13.7 (PS), U13.13 (VDDIO), U15.5 (VIN), U16.P$8 (VCC), U17.2 (VREF1)
+5V: C1.1, C18.1, C19.1, D1.A, D4.A, J3.5, Q2.4 (S), Q4.6 (E1), Q5.2 (S), R8.1, R15.1, T1.1, U1.5 (VIN), U3.9 (VOUT)
BIAS_GND: C16.N (-), C17.1, J4.3, R7.1, T1.7, T1.8
BIAS_V: C16.P (+), D3.C, J4.4, R7.2
CAM1_C_N: J4.24, J6.8 (CAM1_CN)
CAM1_C_P: J4.25, J6.9 (CAM1_CP)
CAM1_D0_N: J4.18, J6.2 (CAM1_DN0)
CAM1_D0_P: J4.19, J6.3 (CAM1_DP0)
CAM1_D1_N: J4.21, J6.5 (CAM1_DN1)
CAM1_D1_P: J4.22, J6.6 (CAM1_DP1)
CAM_CLK: J4.28, J6.12 (CAM_GPIO1)
CAM_GPIO: J4.27, J6.11 (CAM_GPIO0)
C_3V3: J4.31, J6.15 (3V3)
C_SCL0: J4.29, J6.13 (SCL0)
C_SDA0: J4.30, J6.14 (SDA0)
DEBUG_5V: J3.1, Q2.3 (D)
DEC0: U12.15, U14.22 (DEC0)
DEC1: U12.13, U14.24 (DEC1)
DIR: U12.12, U14.13 (DIR)
EN_28V: U1.1 (EN/UVLO), U6.41 (PA28/EIC)
EXTERNAL_3V3: J4.15, Q3.3 (D)
EXTERNAL_KILL: Q2.2 (G), Q3.2 (G), R13.1, R22.1, U6.22 (PA13/I2C/EIC/SCOM2PAD1+/TC2), U16.P$5 (EN)
FB_5: C11.2, C14.2, R8.2, R9.1, R10.1, U3.3 (FB)
GND: B1.3 (-), C1.2, C2.2, C3.2, C4.2, C5.2, C7.2, C8.2, C9.2, C10.2, C12.2, C15.2, C17.2, C19.2, C20.2, C21.2, C22.2, C23.2, C24.2, C25.2, C26.2, C27.2, C28.2, C29.2, C30.2, C31.2, C32.2, C33.2, C34.2, C35.2, C36.2, C37.2, C38.2, C39.2, C40.2, C41.2, C42.2, J1.3, J1.4, J1.5, J2.6 (SD_GND), J2.G1 (GND), J2.G2 (GND), J2.G3 (GND), J3.2, J3.6, J3.14, J4.9, J4.14, J4.17, J4.20, J4.23, J4.26, J5.6 (GND), J5.9 (GND), J5.14 (GND), J5.20 (GND), J5.25 (GND), J5.30 (GND), J5.34 (GND), J5.39 (GND), J6.1 (GND1), J6.4 (GND2), J6.7 (GND3), J6.10 (GND4), JP1.1, JP3.3, JP3.5, Q1.1 (S), Q2.1 (S), Q3.1 (S), R4.1, R5.2, R9.2, R11.2, R13.2, R17.2, R20.1, R21.1, R22.2, R31.1, R32.1, U1.2 (GND), U2.2 (GND), U3.1 (GND), U3.4 (OVP), U3.10 (GND), U3.11 (GND), U3.20 (GND), U3.PAD (GND), U4.5 (GND), U5.10 (VSS), U6.5 (GNDANA), U6.18 (GND1), U6.35 (GND2), U6.42 (GND3), U7.2 (GND), U8.2 (GND), U8.4 (GND), U8.5 (GND), U9.1 (OE), U9.3 (GND), U10.8 (VSS), U10.13 (MODE), U11.4 (GND), U11.5 (A2), U11.6 (A1), U11.7 (A0), U11.9 (EP), U12.9 (GND), U12.25 (EPAD), U13.4 (GNDA), U13.6 (GNDIO), U13.12 (SDO2), U13.17 (SDO1), U13.20 (CSB3), U14.18 (GND), U14.PPAD (GND), U15.1 (OE), U15.3 (GND), U16.P$4 (GND), U17.1 (GND)
I0: U12.17, U14.20 (I0)
I1: U12.16, U14.21 (I1)
IMUDR: U10.9 (DIN), U13.2 (DRDYM)
IMUINT1: U10.5 (BIN), U13.19 (INT1)
IMUINT2: U10.7 (CIN), U13.1 (INT2)
IMUINT3: U10.3 (AIN), U13.14 (INT3)
IMUINT4: U10.11 (EIN), U13.15 (INT4)
IMUINT5: U10.14 (FIN), U13.10 (INT5)
IOEINT: U6.26 (PA17/I2C/EIC/SCOM1PAD1+/TC2), U15.4 (Y)
I_SENSE: C12.1, R5.1, U3.8 (IOUT), U6.10 (PA05/EIC/AIN5/SCOM0PAD1)
LED_CTRL: U2.4 (EN), U6.14 (PA09/I2C/EIC/AIN17/SCOM2PAD1+/TC0)
LED_GND: J4.2, R4.2, U2.3 (FB)
LED_V: C15.1, J4.1, U2.1 (V_OUT)
M0: U12.11, U14.8 (M0)
M1: U12.10, U14.9 (M1)
MA1: J4.5, U14.1 (AOUT1)
MA2: J4.6, U14.3 (AOUT2)
MB1: J4.7, U14.6 (BOUT1)
MB2: J4.8, U14.4 (BOUT2)
MISO: J2.7 (DATA_OUT), U5.8 (DQ1), U6.21 (PA12/I2C/EIC/SCOM2PAD0+/TC2)
MOSI: J2.3 (DATA_IN), U5.15 (DQ0), U6.19 (PB10/EIC/SCOM4PAD2/TC5)
unnamed: Q4.4 (C2), Q5.1 (G), R32.2
unnamed: Q4.1 (C1), Q4.2 (B1), Q4.3 (B2), R31.2
unnamed: R33.1, U3.19 (PWM/SYNC)
unnamed: C25.1, L5.2, U6.17 (VDDIO1)
unnamed: C27.1, U6.43 (VDDCORE)
unnamed: R23.1, U11.3 (OS)
unnamed: JP1.2, R1.1
unnamed: B1.1 (+), B1.2 (+), C5.1, U4.6 (VBAT)
unnamed: C29.1, U7.4 (BYP)
unnamed: C21.1, C22.1, FB1.2, U6.6 (VDDANA)
unnamed: C14.1, R6.1
unnamed: C11.1, R6.2, U3.2 (COMP)
unnamed: C20.1, L3.2, U6.44 (VCC)
unnamed: L1.P$2 (2), U2.6 (SW)
unnamed: R29.1, U14.19 (ADEC)
unnamed: Q3.5 (G), Q3.6 (D), R24.2
unnamed: U10.2 (AOUT), U12.1 (P00)
unnamed: R21.2, U14.5 (BISEN)
unnamed: R20.2, U14.2 (AISEN)
unnamed: U9.4 (Y), U14.12 (STEP)
unnamed: U10.4 (BOUT), U12.2 (P01)
unnamed: C23.1, C26.1, L4.2, U6.36 (VDDIO2)
unnamed: U12.22 (INT), U15.2 (A)
unnamed: C38.1, U14.14 (VREF), U14.17 (VINT)
unnamed: U10.6 (COUT), U12.3 (P02)
unnamed: U10.10 (DOUT), U12.4 (P03)
unnamed: U10.12 (EOUT), U12.5 (P04)
unnamed: U10.15 (FOUT), U12.6 (P05)
unnamed: R14.2, U5.1 (DQ3/!HOLD!), U5.3 (!RESET!)
unnamed: R27.1, U12.20 (SDA), U17.8 (SDA2)
unnamed: R25.1, U12.19 (SCL), U17.7 (SCL2)
unnamed: C41.1, R26.1, U17.5 (EN), U17.6 (VREF2)
unnamed: Q1.5 (G), Q1.6 (D), R12.2
unnamed: Q2.5 (G), Q2.6 (D), R15.2
unnamed: C6.1, L2.P$1, U3.15 (SW1), U3.16 (SW1)
unnamed: C13.1, L2.P$2, U3.12 (SW2), U3.13 (SW2)
unnamed: C6.2, U3.17 (BST1)
unnamed: C13.2, U3.14 (BST2)
unnamed: C4.1, D4.C, R33.2, U3.18 (VCC)
unnamed: C18.2, R10.2
unnamed: R2.2, U1.3 (RFB)
unnamed: D2.A, R2.1, T1.4, U1.4 (SW)
unnamed: D1.C, D2.C
unnamed: D3.A, T1.5, T1.6
NENBL: R19.2, U12.8 (P07), U14.11 (NENBL)
NFAULT: R18.2, U12.7 (P06), U14.7 (NFAULT)
NSLEEP: U12.14, U14.23 (NSLEEP)
PA27: U4.3 (!INT!/SQW), U6.39 (PA27/EIC)
PB02: U6.47 (PB02/EIC/AIN10/SCOM5PAD0), U8.8 (INT1)
PB03: U6.48 (PB03/EIC/AIN11/SCOM5PAD1), U8.9 (INT2)
PB22: J2.2 (CS), U6.37 (PB22/EIC/SCOM5PAD2)
PB23: U5.7 (!S!), U6.38 (PB23/EIC/SCOM5PAD3)
PI_5V: J5.2 (5V), J5.4 (5V), Q1.3 (D)
PI_D_N: J3.7, TP2.P$1
PI_D_P: J3.8, TP1.P$1
PI_KILL: Q1.2 (G), R11.1, U6.25 (PA16/I2C/EIC/SCOM1PAD0+/TC2)
RESET: C10.1, JP3.10, R1.2, R3.1, U6.40 (RESET)
RX0: J1.6, U6.16 (PA11/EIC/AIN19/SCOM2PAD3+/TC1)
RX1: J5.8 (BCM14(TXD)), U6.28 (PA19/EIC/SCOM1PAD3+/TC3)
RX2: J3.9, U6.30 (PA21/EIC/SCOM5PAD3+)
SCK: J2.5 (SCLK), U5.16 (C), U6.20 (PB11/EIC/SCOM4PAD3/TC5)
SCL: R28.3 (1), U4.8 (SCL), U6.32 (PA23/I2C/EIC/SCOM5PAD1+/TC4), U8.14 (SCL/SCLK), U11.2 (SCL), U13.9 (SCX), U16.P$2 (SCL0), U17.3 (SCL1)
SCL_BUFF: J4.12, R28.2 (1), U16.P$7 (SCL1)
SDA: R28.4 (1), U4.7 (SDA), U6.31 (PA22/I2C/EIC/SCOM5PAD0+/TC4), U8.13 (SDA/SDI/SDIO), U11.1 (SDA), U13.11 (SDX), U16.P$3 (SDA0), U17.4 (SDA1)
SDA_BUFF: J4.13, R28.1, U16.P$6 (SDA1)
STEPFREQ: U6.13 (PA08/I2C/AIN16/SCOM2PAD0+/TC0), U9.2 (A)
SWDCLK: JP3.4, R30.1, U6.45 (PA30/EIC/SCOM1PAD2/SWDCLK)
SWDIO: JP3.2, U6.46 (PA31/EIC/SCOM1PAD3/SWDIO)
SYNC: J5.37 (BCM26), U6.24 (PA15/XOUT/EIC/SCOM2PAD3+/TC3)
TX0: J1.7, U6.15 (PA10/EIC/AIN18/SCOM2PAD2+/TC1)
TX1: J5.10 (BCM15(RXD)), U6.27 (PA18/EIC/SCOM1PAD2+/TC3)
TX2: J3.10, U6.29 (PA20/EIC/SCOM5PAD2+)
USB_D_N: J3.4, U6.33 (PA24/EIC/SCOM3PAD2+/TC5)
USB_D_P: J3.3, U6.34 (PA25/EIC/SCOM3PAD3+/TC5)
VCC: C2.1, C42.1, J1.1, J1.2, U3.5 (VIN), U3.6 (VIN), U3.7 (RUN)
VREFA: C35.1, L6.1, U6.4 (PA03/EIC/REF/AI/VREFA)
V_SENSE: R16.2, R17.1, U6.3 (PA02/EIC/AIN)
XIN32: C7.1, U6.1 (PA00/XIN32/EIC/SCOM1PAD0), XTAL1.P2 (2)
XOUT32: C8.1, U6.2 (PA01/XOUT32/EIC/SCOM1PAD1), XTAL1.P1 (1)

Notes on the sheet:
MICROCONTROLLER BLOCK
Cortex Debug Connector
RESET SWITCH
XTAL
AREF
V SENSE
I2C PULLUPS
HIGH G ACCEL
TEMP SENSOR
REAL TIME CLOCK
IMU
MICRO SD CARD
ONBOARD FLASH
LED DRIVER
MOTOR DRIVER
MULTIPLEXER
PI CUTOFF
DEBUG CUTOFF
I2C BUFFER
EXTERNAL POWER KILL
28V BIAS
3.3V LDO
5V SUPPLY
HERMES MDM
DEBUG MDM
PAYLOAD MDM
RPI-CSI
RPI
5V PROTECT

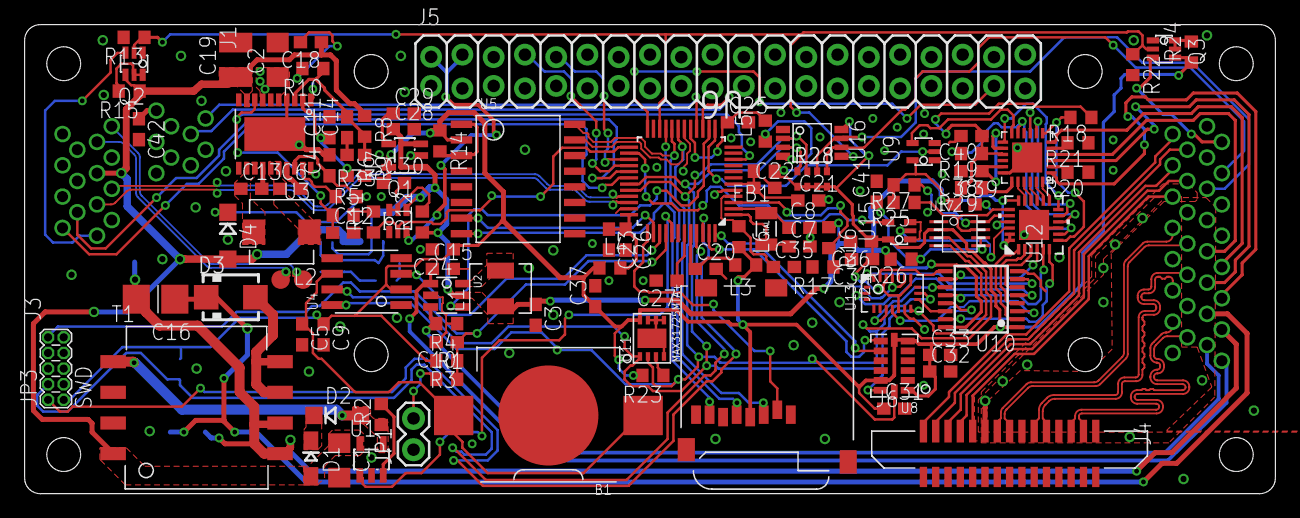
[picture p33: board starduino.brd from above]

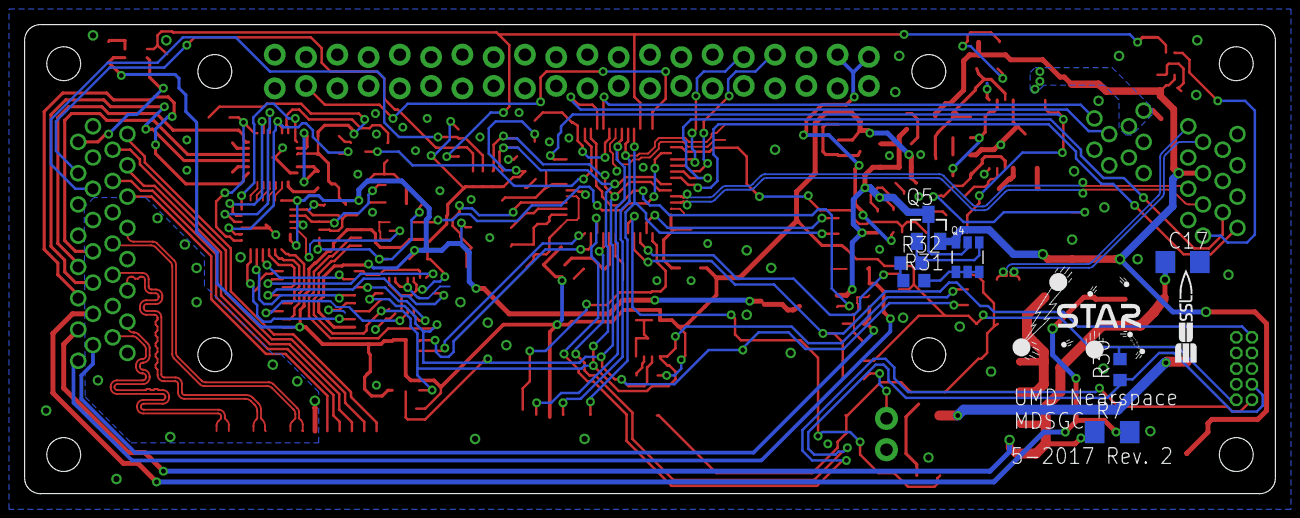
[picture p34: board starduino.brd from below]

Board: 2 copper layers, 101.6 x 38.1 mm, 123 parts (9 on the bottom side), 125 nets.

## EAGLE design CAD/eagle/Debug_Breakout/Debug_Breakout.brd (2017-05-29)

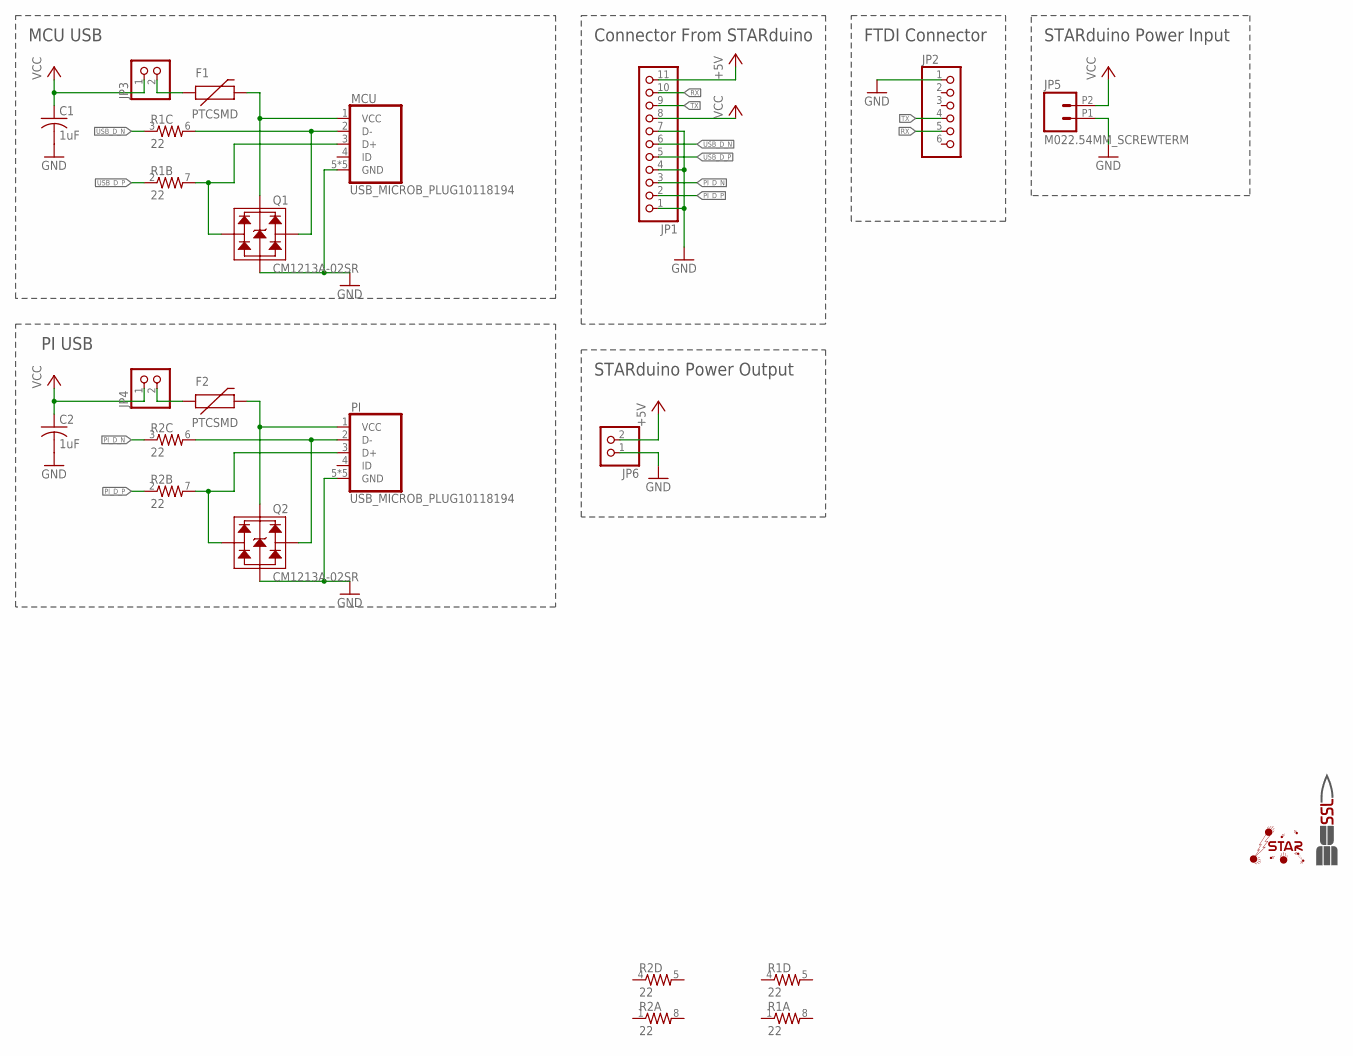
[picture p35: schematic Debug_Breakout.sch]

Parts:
C1, C2: 1uF; C0603
F1, F2: PTCSMD; PTC-1206
JP1: PINHD-1X11; 1X11
JP2: PINHD-1X6; 1X06
JP3, JP4, JP6: PINHD-1X2; 1X02
JP5: M022.54MM_SCREWTERM; 1X02_2.54_SCREWTERM
MCU: USB_MICROB_PLUG10118194; MICRO-B-10118194
PI: USB_MICROB_PLUG10118194; MICRO-B-10118194
Q1, Q2: CM1213A-02SR; SOT143-4
R1, R2: 22; 0603-ARV
U$1: SSL.3IN_SILK; SSL_SILK_.3IN
U$2: STAR; STAR_.3IN

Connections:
+5V: JP1.11, JP6.2
GND: C1.2, C2.2, JP1.1, JP1.4, JP1.7, JP2.1, JP5.P1 (1), JP6.1, MCU.5 (GND), MCU.S1 (GND), MCU.S2 (GND), MCU.S3 (GND), MCU.S4 (GND), PI.5 (GND), PI.S1 (GND), PI.S2 (GND), PI.S3 (GND), PI.S4 (GND), Q1.P$1 (GND), Q2.P$1 (GND)
MCU_D_N: MCU.2 (D-), Q1.P$3 (CH2), R1.6 (2)
MCU_D_P: MCU.3 (D+), Q1.P$2 (CH1), R1.7 (2)
unnamed: F2.2, PI.1 (VCC), Q2.P$4 (VCC)
unnamed: F1.2, MCU.1 (VCC), Q1.P$4 (VCC)
unnamed: F2.1, JP4.2
unnamed: F1.1, JP3.2
PICONN_D_N: PI.2 (D-), Q2.P$3 (CH2), R2.6 (2)
PICONN_D_P: PI.3 (D+), Q2.P$2 (CH1), R2.7 (2)
PI_D_N: JP1.3, R2.3 (1)
PI_D_P: JP1.2, R2.2 (1)
RX: JP1.10, JP2.5
TX: JP1.9, JP2.4
USB_D_N: JP1.6, R1.3 (1)
USB_D_P: JP1.5, R1.2 (1)
VCC: C1.1, C2.1, JP1.8, JP3.1, JP4.1, JP5.P2 (2)

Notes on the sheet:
MCU USB
PI USB
Connector From STARduino
STARduino Power Output
STARduino Power Input
FTDI Connector

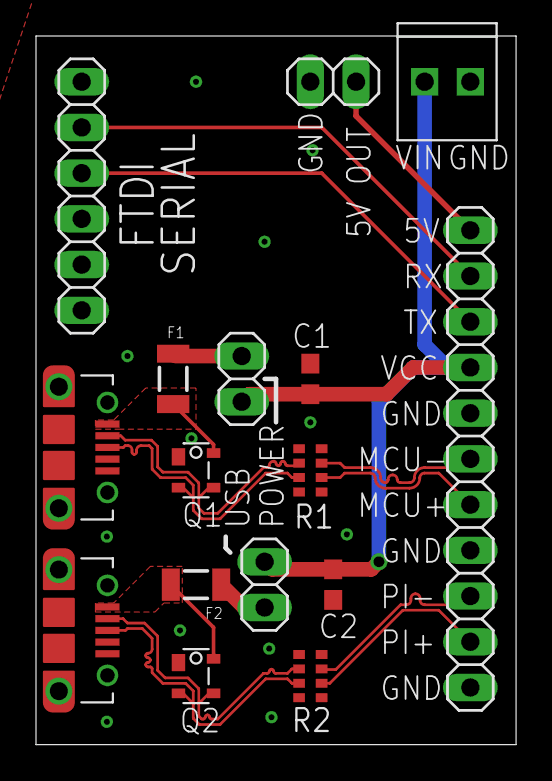
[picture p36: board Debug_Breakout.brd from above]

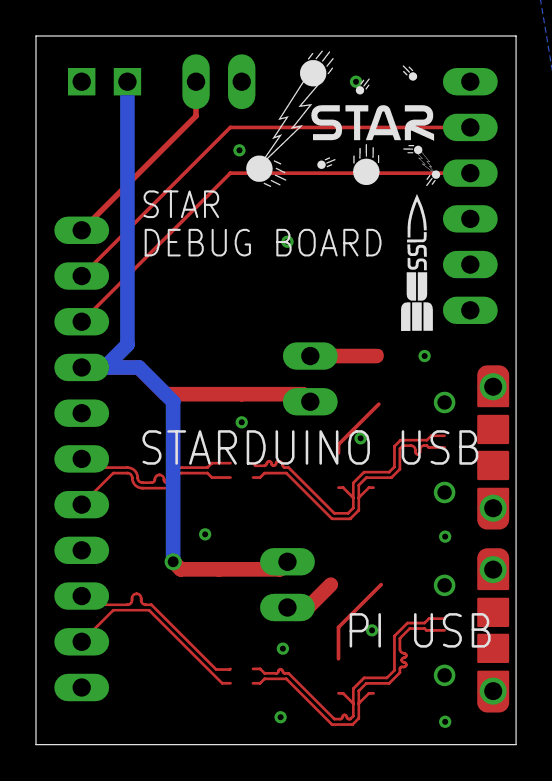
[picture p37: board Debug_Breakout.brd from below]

Board: 2 copper layers, 26.7 x 39.4 mm, 18 parts (2 on the bottom side), 17 nets.

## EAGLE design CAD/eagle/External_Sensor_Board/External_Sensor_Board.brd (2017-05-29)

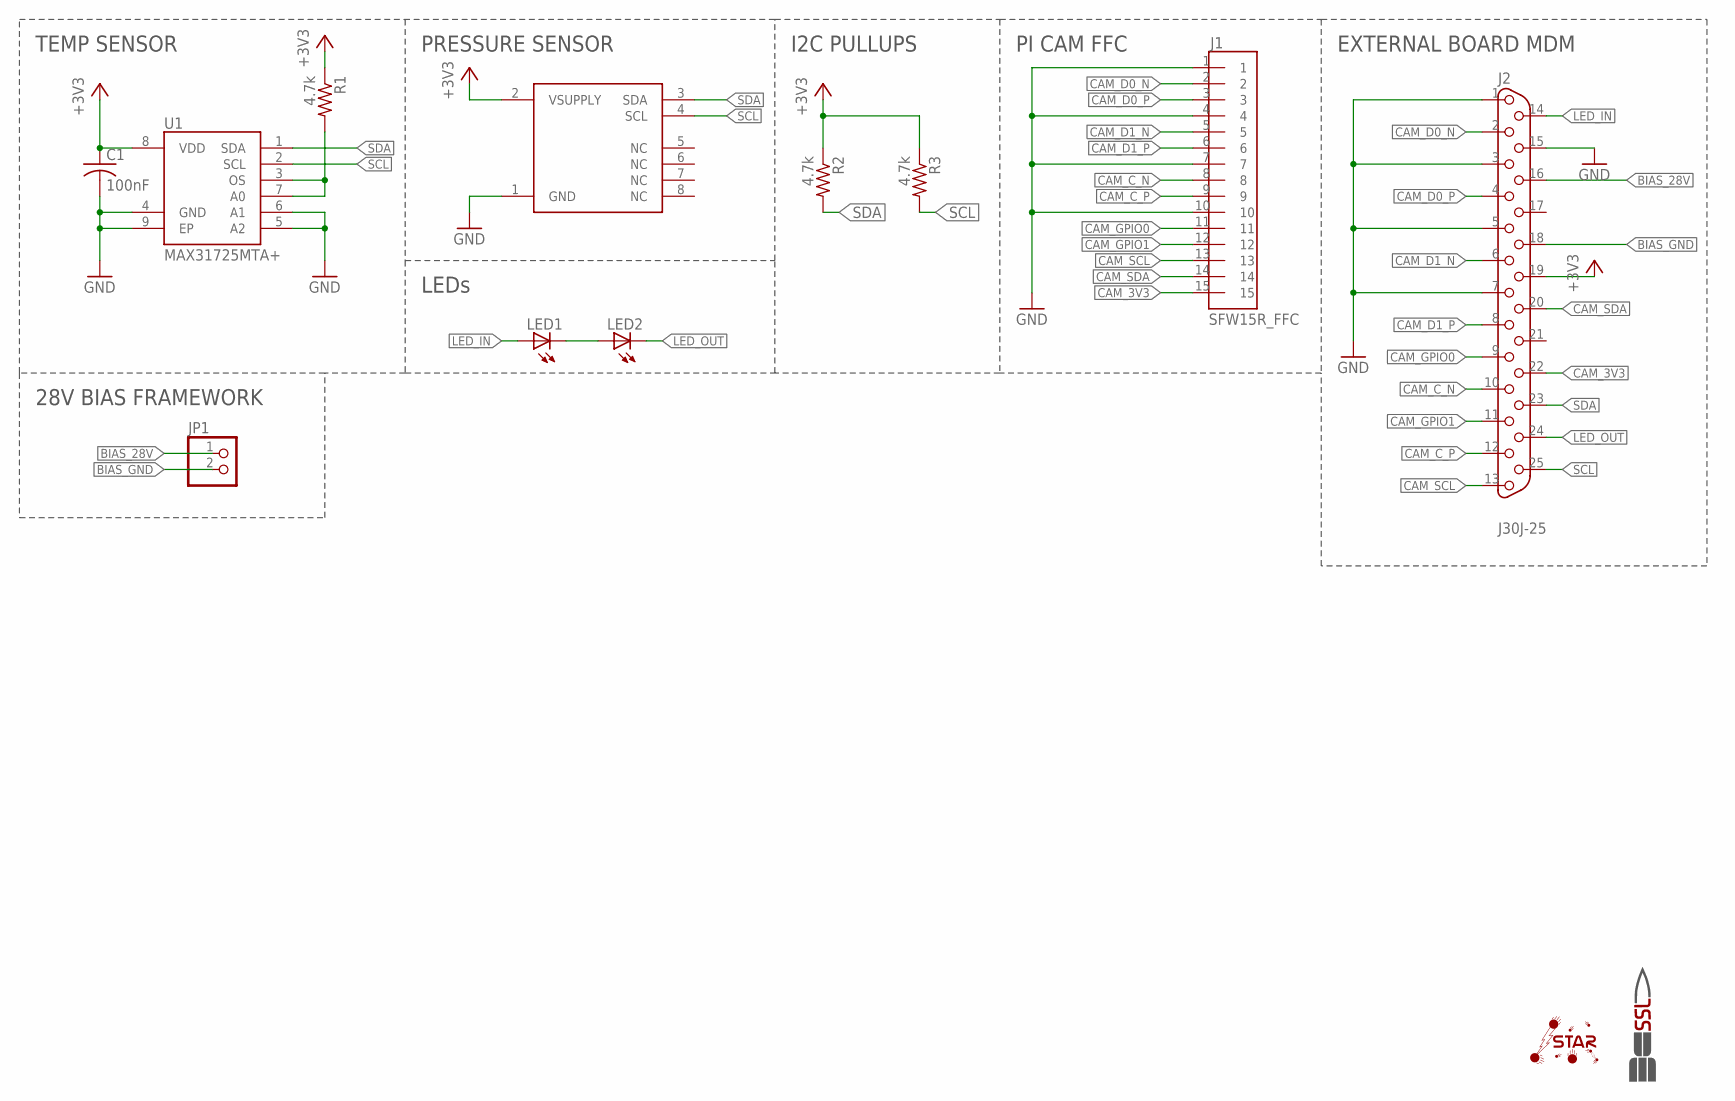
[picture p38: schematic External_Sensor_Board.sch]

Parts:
C1: 100nF; C0603
J1: SFW15R_FFC; AMPHENOL_15_FFC
J2: J30J-25; ZKN-25
JP1: PINHD-1X2; 1X02
LED1, LED2: LED_1206_NS; 1206_NS
R1, R2, R3: 4.7k; R0603
U1: MAX31725MTA+; DFN-8
U2: SSCMNNN015PA2A3; HSC-SMT-8
U$1: SSL.3IN_SILK; SSL_SILK_.3IN
U$2: STAR; STAR_.3IN

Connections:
+3V3: C1.1, J2.19, R1.1, R2.1, R3.1, U1.8 (VDD), U2.2 (VSUPPLY)
BIAS_28V: J2.16, JP1.1
BIAS_GND: J2.18, JP1.2
CAM_3V3: J1.15, J2.22
CAM_C_N: J1.8, J2.10
CAM_C_P: J1.9, J2.12
CAM_D0_N: J1.2, J2.2
CAM_D0_P: J1.3, J2.4
CAM_D1_N: J1.5, J2.6
CAM_D1_P: J1.6, J2.8
CAM_GPIO0: J1.11, J2.9
CAM_GPIO1: J1.12, J2.11
CAM_SCL: J1.13, J2.13
CAM_SDA: J1.14, J2.20
GND: C1.2, J1.1, J1.4, J1.7, J1.10, J2.1, J2.3, J2.5, J2.7, J2.15, U1.4 (GND), U1.5 (A2), U1.6 (A1), U1.9 (EP), U2.1 (GND)
LED_IN: J2.14, LED1.2 (A)
LED_OUT: J2.24, LED2.1 (C)
unnamed: R1.2, U1.3 (OS), U1.7 (A0)
unnamed: LED1.1 (C), LED2.2 (A)
SCL: J2.25, R3.2, U1.2 (SCL), U2.4 (SCL)
SDA: J2.23, R2.2, U1.1 (SDA), U2.3 (SDA)

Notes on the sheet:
TEMP SENSOR
PRESSURE SENSOR
I2C PULLUPS
PI CAM FFC
EXTERNAL BOARD MDM
LEDs
28V BIAS FRAMEWORK

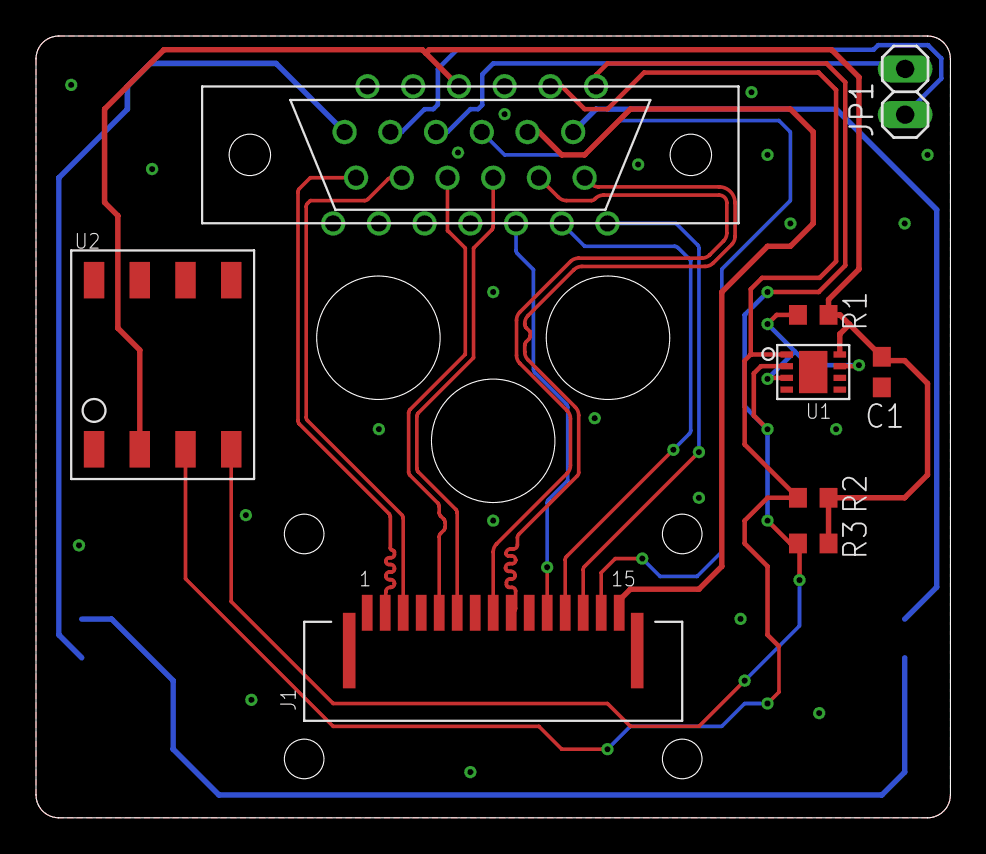
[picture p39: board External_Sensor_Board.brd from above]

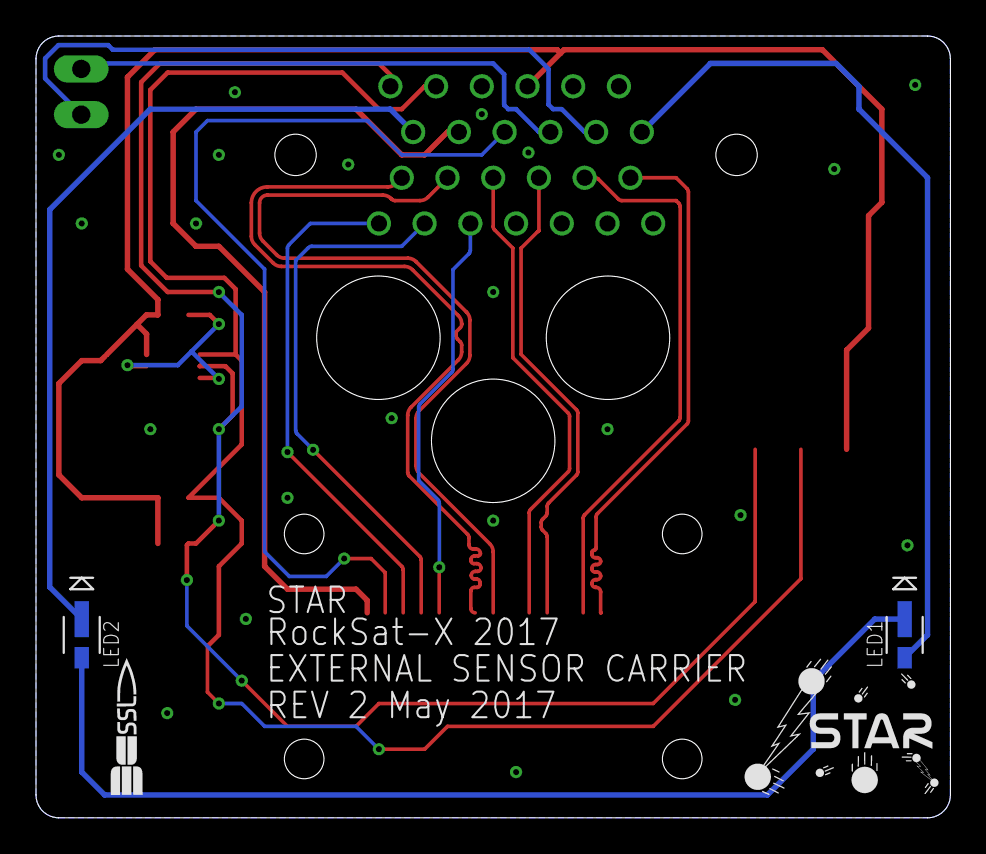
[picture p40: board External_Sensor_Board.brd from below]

Board: 2 copper layers, 50.8 x 43.4 mm, 13 parts (4 on the bottom side), 21 nets.

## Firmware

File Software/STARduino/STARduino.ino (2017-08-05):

#define CUTOFF_TIME_MILLISECONDS 600000

#include "EZGPIO.h"
#include<Wire.h>
#include "src/Sensors/ADXL375.h"
#include "src/Sensors/MAX31725Temp.h"
#include "src/Sensors/PowerSensors.h"
#include "src/Sensors/BMX055.h"
#include <SPI.h>
#include<SD.h>


uint8_t LEDPIN = 9;
uint8_t BIASPIN = 28;
uint8_t PIKILL = 16;
uint8_t EXTKILL = 13;
uint8_t SDCSPIN = 22;
uint8_t FLASHCSPIN = 23;

ADXL375 adxl;
MAX31725 tempSensor;
VoltageSense voltageSensor;
CurrentSense currentSensor;
BMX055_ACCEL bmxAccel;
BMX055_GYRO bmxGyro;
BMX055_MAG bmxMag;


/* Define Functions */
void setup() {
  /*
     Initalizes the STAR payload. Opens the serial connections, opens log files,
     loads queued commands, and initializes sensors.

     Inputs:
     none

     Output:
     none

     Return:
     none

  */
  Serial.begin(9600);
  Wire.begin();
  
  for(int i = 0; i < 10; i ++)
  {
    Serial.print("Here: ");
    Serial.println(i);
    
  }
  
  
  Serial.println("Began");

  // Enable ESB; 
  
  DIRSET_A = (1 << EXTKILL);
  OUTSET_A = (1 << EXTKILL);
  DIRSET_A = (1 << LEDPIN);
  OUTSET_A = (1 << LEDPIN);
  DIRSET_A = (1 << BIASPIN);
  OUTSET_A = (1 << BIASPIN);

  DIRSET_B = (1 << SDCSPIN);
  DIRSET_B = (1 << FLASHCSPIN);
  OUTCLR_B = (1 << SDCSPIN);
  OUTSET_B = (1 << FLASHCSPIN);

  Serial.print("Initializing SD card...");
  // see if the card is present and can be initialized:
  if (!SD.begin(4)) {
    Serial.println("Card failed, or not present");
    // don't do anything more:
    return;
  }
  else
  {
    Serial.println("card initialized.");
  }

  // Not all sensors require begin() functions
  adxl.begin();
  bmxMag.begin();

  File dataFile = SD.open("datalog.txt", FILE_WRITE);

  if (dataFile) {
    dataFile.println("MDSGC Rocksat-X Data Log");
    dataFile.close();
  }
  else {
    Serial.println("error opening datalog.txt");
  }

}

void loop() {
    

    uint32_t sensorReadingTime = millis();

    if(sensorReadingTime > CUTOFF_TIME_MILLISECONDS)
    {
      OUTCLR_A = (1 << LEDPIN);
      OUTCLR_A = (1 << EXTKILL);
      OUTCLR_A = (1 << BIASPIN);
    }
    
    uint16_t adcVoltageReading = voltageSensor.read_voltage();
    uint16_t adcCurrentReading = currentSensor.read_current();
  
    adxl.recieve_data();
    int16_t adxlAccelerometerXReading = adxl.get_x_accel();
    int16_t adxlAccelerometerYReading = adxl.get_y_accel();
    int16_t adxlAccelerometerZReading = adxl.get_z_accel();
    
    tempSensor.recieve_data();
    uint16_t maximTemperatureReading = tempSensor.get_temperature();
    
    bmxAccel.recieve_data();
    int16_t bmxAccelerometerXReading = bmxAccel.get_x_accel();
    int16_t bmxAccelerometerYReading = bmxAccel.get_y_accel();
    int16_t bmxAccelerometerZReading = bmxAccel.get_z_accel();
    int16_t bmxAccelerometerTemperatureReading = bmxAccel.get_temp();

    bmxGyro.recieve_data();
    int16_t bmxGyroscopeXReading = bmxGyro.get_x_gyro();
    int16_t bmxGyroscopeYReading = bmxGyro.get_y_gyro();
    int16_t bmxGyroscopeZReading = bmxGyro.get_z_gyro();

    bmxMag.recieve_data();
    int16_t bmxMagnetometerXReading = bmxMag.get_x_mag();
    int16_t bmxMagnetometerYReading = bmxMag.get_y_mag();
    int16_t bmxMagnetometerZReading =  bmxMag.get_z_mag();
    uint16_t bmxMagnetometerHallReading = bmxMag.get_hall();
    
    uint32_t portADir = PORT->Group[0].DIR.reg;
    uint32_t portBDir = PORT->Group[1].DIR.reg;
    uint32_t portAOut = PORT->Group[0].OUTSET.reg; // TODO HACK
    uint32_t portBOut = PORT->Group[1].OUTSET.reg; // TODO HACK
      
   File dataFile = SD.open("datalog.txt", FILE_WRITE);

  // if the file is available, write to it:
  if (dataFile) {
    dataFile.print(sensorReadingTime);
    dataFile.print(",");
    dataFile.print(portADir);
    dataFile.print(",");
    dataFile.print(portBDir);
    dataFile.print(",");
    dataFile.print(portAOut);
    dataFile.print(",");
    dataFile.print(portBOut);
    dataFile.print(",");
    dataFile.print(adcVoltageReading);
    dataFile.print(",");
    dataFile.print(adcCurrentReading);
    dataFile.print(",");
    dataFile.print(adxlAccelerometerXReading);
    dataFile.print(",");
    dataFile.print(adxlAccelerometerYReading);
    dataFile.print(",");
    dataFile.print(adxlAccelerometerZReading);
    dataFile.print(",");
    dataFile.print(maximTemperatureReading);
    dataFile.print(",");
    dataFile.print(bmxAccelerometerXReading);
    dataFile.print(",");
    dataFile.print(bmxAccelerometerYReading);
    dataFile.print(",");
    dataFile.print(bmxAccelerometerZReading);
    dataFile.print(",");
    dataFile.print(bmxAccelerometerTemperatureReading);
    dataFile.print(",");
    dataFile.print(bmxGyroscopeXReading);
    dataFile.print(",");
    dataFile.print(bmxGyroscopeYReading);
    dataFile.print(",");
    dataFile.print(bmxGyroscopeZReading);
    dataFile.print(",");
    dataFile.print(bmxMagnetometerXReading);
    dataFile.print(",");
    dataFile.print(bmxMagnetometerYReading);
    dataFile.print(",");
    dataFile.print(bmxMagnetometerZReading);
    dataFile.print(",");
    dataFile.print(bmxMagnetometerHallReading);
    dataFile.println();
    dataFile.close();
    
  }
  // if the file isn't open, pop up an error:
  else {
    Serial.println("error opening datalog.txt");
  }

  
}

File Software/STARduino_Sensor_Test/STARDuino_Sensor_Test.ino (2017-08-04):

#include "EZGPIO.h"
#include<Wire.h>




#define TEST_ALL_SENSORS
//#define LOG_TEST

#ifdef TEST_ALL_SENSORS
  //#define ADXL_TEST
  //#define MAX_TEMP_TEST
  //#define POWER_SENSOR_TEST
  #define BMX_ACCEL_TEST
  //#define BMX_GYRO_TEST
  #define BMX_MAG_TEST
#endif


int LEDPIN = 9;
int BIASPIN = 28;
int PIKILL = 16;
int EXTKILL = 13;
int SDCSPIN = 22;

#ifdef ADXL_TEST
  #include "src/Sensors/ADXL375.h"
  ADXL375 adxl;
#endif

#ifdef MAX_TEMP_TEST
  #include "src/Sensors/MAX31725Temp.h"
  MAX31725 tempSensor;
#endif

#ifdef POWER_SENSOR_TEST
  #include "src/Sensors/PowerSensors.h"
  VoltageSense voltageSensor;
  CurrentSense currentSensor;
#endif

#ifdef BMX_ACCEL_TEST
  #include "src/Sensors/BMX055.h"
  BMX055_ACCEL bmxAccel;
#endif


#ifdef BMX_GYRO_TEST
  #include "src/Sensors/BMX055.h"
  BMX055_GYRO bmxGyro;
#endif

#ifdef BMX_MAG_TEST
  #include "src/Sensors/BMX055.h"
  BMX055_MAG bmxMag;
#endif

#ifdef LOG_TEST
  #include <SPI.h>
  #include<SD.h>
#endif

/* Define Functions */
void setup() {
  /*
     Initalizes the STAR payload. Opens the serial connections, opens log files,
     loads queued commands, and initializes sensors.

     Inputs:
     none

     Output:
     none

     Return:
     none

  */
    delay(3000);
  Serial.begin(9600);
  Wire.begin();
  Serial.println("Began");
  
  // Pull "Kill" ports high:
  DIRSET_A = (1 << PIKILL);
  OUTSET_A = (1 << PIKILL);
  DIRSET_A = (1 << EXTKILL);
  OUTSET_A = (1 << EXTKILL);

  DIRSET_B = (1 << SDCSPIN);
  OUTCLR_B = (1 << SDCSPIN);

  #ifdef BMX_MAG_TEST

      uint8_t powerControlReg = 0x4B;
    uint8_t opReg = 0x4C;
    uint8_t opVal = 0x0;
    uint8_t powerConrolValue = 0x01;
    uint8_t val = 0x0;
    
    //Serial.println("==================");
  


    //uint8_t outVal = 255;
    
    //Serial.println(outVal);


    //uint8_t result = bmxMag.read_register(powerControlReg, outVal);
    //Serial.println(outVal);
    
    bmxMag.begin();
    //bmxMag.write_register(powerControlReg, powerConrolValue);
    //bmxMag.write_register(opReg, opVal);
    
    
    
   // result = bmxMag.read_register(powerControlReg, outVal);
   // Serial.println(outVal);
    //result = bmxMag.read_register(opReg, outVal);
    //Serial.println(outVal);
    //Serial.println("==================");
      
  #endif

#ifdef LOG_TEST
  Serial.print("Initializing SD card...");
  // see if the card is present and can be initialized:
  if (!SD.begin(4)) {
    Serial.println("Card failed, or not present");
    // don't do anything more:
    return;
  }
  else
  {
    Serial.println("card initialized.");
  }
  #endif
  
  //DIRSET_A = (1 << BIASPIN);
  //DIRSET_A = (1 << LEDPIN);
}

void loop() {

  #ifdef ADXL_TEST
    adxl.begin();
    

    uint8_t data = 0xFF;;
    adxl.read_register(0x2D , data);
    Serial.print("Register: 0x");
    Serial.println(data, HEX);

    adxl.recieve_data();

    int16_t rawXAcc = adxl.get_x_accel();
    int16_t rawYAcc = adxl.get_y_accel();
    int16_t rawZAcc = adxl.get_z_accel();
    
    Serial.print("Raw ADXL X acceleration: ");
    Serial.println(rawXAcc);
    Serial.print("Raw ADXL Y acceleration: ");
    Serial.println(rawYAcc);
    Serial.print("Raw ADXL Z acceleration: ");
    Serial.println(rawZAcc);

    Vector3<float> convertedAdxlAcceleration = adxl.convert_data();

    Serial.print("Converted ADXL X acceleration: ");
    Serial.println(convertedAdxlAcceleration.x);
    Serial.print("Converted ADXL Y acceleration: ");
    Serial.println(convertedAdxlAcceleration.y);
    Serial.print("Convertedaw ADXL Z acceleration: ");
    Serial.println(convertedAdxlAcceleration.z);
    
  #endif
  
  #ifdef MAX_TEMP_TEST
    
    tempSensor.recieve_data();
    uint8_t tempConfigRegister = tempSensor.read_config_register();
    uint16_t rawTemp = tempSensor.get_temperature();
    float convertedTemp = tempSensor.convert_temp();
    Serial.print("MAX31725 Configuration Register: ");
    Serial.println(tempConfigRegister);
    Serial.print("Raw MAX31725 temperature: ");
    Serial.println(rawTemp);
    Serial.print("Converted MAX31725 Temperature: ");
    Serial.println(convertedTemp);
  #endif 


  #ifdef POWER_SENSOR_TEST
    uint16_t rawVoltage = voltageSensor.read_voltage();
    uint16_t rawCurrent = currentSensor.read_current();
    Serial.print("Raw voltage: ");
    Serial.println(rawVoltage);
    Serial.print("Raw current: ");
    Serial.println(rawCurrent);
  #endif

  #ifdef BMX_ACCEL_TEST
    bmxAccel.recieve_data();
      
    int16_t bmxRawXAcc = bmxAccel.get_x_accel();
    int16_t bmxRawYAcc = bmxAccel.get_y_accel();
    int16_t bmxRawZAcc = bmxAccel.get_z_accel();
    int16_t bmxTemp = bmxAccel.get_temp();
    
    Serial.print("Raw BMX X acceleration: ");
    Serial.println(bmxRawXAcc);
    Serial.print("Raw BMX Y acceleration: ");
    Serial.println(bmxRawYAcc);
    Serial.print("Raw BMX Z acceleration: ");
    Serial.println(bmxRawZAcc);
    Serial.print("Raw BMX temp: ");
    Serial.println(bmxTemp);
  #endif

  #ifdef BMX_GYRO_TEST
    bmxGyro.recieve_data();
      
    int16_t xRate = bmxGyro.get_x_gyro();
    int16_t yRate = bmxGyro.get_y_gyro();
    int16_t zRate = bmxGyro.get_z_gyro();
    
    Serial.print("Raw BMX X rate: ");
    Serial.println(xRate);
    Serial.print("Raw BMX Y rate: ");
    Serial.println(yRate);
    Serial.print("Raw BMX Z rate: ");
    Serial.println(zRate);
  #endif

  #ifdef BMX_MAG_TEST
    bmxMag.recieve_data();

    int16_t xMag = bmxMag.get_x_mag();
    int16_t yMag = bmxMag.get_y_mag();
    int16_t zMag = bmxMag.get_z_mag();
    
    Serial.print("Raw BMX X mag: ");
    Serial.println(xMag);
    Serial.print("Raw BMX Y mag: ");
    Serial.println(yMag);
    Serial.print("Raw BMX Z mag: ");
    Serial.println(zMag);
  #endif

  #ifdef LOG_TEST
   File dataFile = SD.open("datalog.txt", FILE_WRITE);

  // if the file is available, write to it:
  if (dataFile) {
    dataFile.println("Herpaderp");
    dataFile.close();
    // print to the serial port too:
    Serial.println("Herpaderp"0);
  }
  // if the file isn't open, pop up an error:
  else {
    Serial.println("error opening datalog.txt");
  }

  #endif

  delay(200);

}

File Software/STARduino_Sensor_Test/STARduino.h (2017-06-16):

#ifndef _starduino_h_
#define _starduino_h_

/* Include libraries */
#include <SPI.h>
#include <SD.h>
#include <Wire.h>
#include "RTClib.h"

/* Define Parameters */
// used for setting size of buffers which will hold packets
#define MAX_CMD_LEN 100

// used for setting size of queue storage for commands
// Note: Not all commands are allowed to be queued (ex, file 
//  commands), so the size of this buffer only has to hold 
//  the largest queued command.
#define MAX_QUEUE_CMD_LEN 9

// used for setting size of buffer to hold output packets being created
#define MAX_TLM_LEN 255

// cycles that a partial packet will be kept before being discarded
#define MAX_READ_CYCLES_STALENESS 15

// cycles that a partial packet will be kept before being discarded
#define DESIRED_CYCLE_HZ 30

// define the max number of commands allowed in a queue
#define MAX_CMDS_IN_QUEUE 10

// define the number of bytes of a file sent in each packet
#define FILE_BYTES_PER_PKT 100

// alias this to the name StaticQueue expects
#define QUEUE_LEN 10//MAX_CMDS_IN_QUEUE

/* Include project libraries */
#include "src/CCSDS/CCSDS.h"
#include "src/CCSDS/ccsds_utilities.h"
#include "src/Queue/StaticQueue.h"

/* Define aliases */
// Software Reset Register
#define RESET_REGISTER *(unsigned int volatile *)0xE000ED0C

// Serials
#define SERIAL_DEBUG Serial // FIXME
#define SERIAL_CTU Serial
#define SERIAL_PI Serial // FIXME

// Pins
#define PIN_SDCHIPSELECT 53 // FIXME
#define PIN_LEDPWM 14 // FIXME
#define PIN_MOTORPWM 14 // FIXME
#define PIN_BIAS 14 // FIXME
#define PIN_CUTOFF 14 // FIXME

// APIDs
#define APID_STAR_CMD 100
#define APID_STAR_FILELOADERR 110
#define APID_STAR_TXTMSG 120
#define APID_STAR_CMDRESP 130
#define APID_STAR_STATUS 140
#define APID_STAR_FILEINFO 150
#define APID_STAR_FILECHKSUM 160
#define APID_STAR_BEGIN_FILESEND 170
#define APID_STAR_FILEDATA 171
#define APID_STAR_END_FILESEND 172

// FcnCodes
#define FCNCODE_NOOP_CMD 9
#define FCNCODE_LED_CMD 10
#define FCNCODE_BIAS_CMD 11 
#define FCNCODE_SHAKE_CMD 12
#define FCNCODE_CUTOFF_CMD 13
#define FCNCODE_TLM_CMD 14
#define FCNCODE_QUEUE_CMD 15
#define FCNCODE_RESETMET_CMD 16
#define FCNCODE_FILEINFO_CMD 17
#define FCNCODE_REBOOT_CMD 18
#define FCNCODE_SENDFILE_CMD 19
#define FCNCODE_DELFILE_CMD 20
#define FCNCODE_RCVFILE_CMD 22

// Filenames1
#define FILENAME_INTERFACE_LOG "intf_log.txt"
#define FILENAME_SENSOR_LOG "sens_log.txt"
#define FILENAME_SYNC_LOG "sync_log.txt"
#define FILENAME_CMDSEQ "cmds.cmd"

// Errors
#define ERROR_SDLOAD_OPENFILE -1
#define ERROR_SDLOAD_CMDCHKSUM -3
#define ERROR_FLASHLOAD_NOTIMP -5
#define ERROR_SDLOAD_SHORTTIME -6
#define ERROR_SDLOAD_SHORTHEAD -7
#define ERROR_SDLOAD_SHORTPKT -8
#define ERROR_SDLOAD_INFILOOP -9
#define ERROR_SDLOAD_SUCCESS 0
#define ERROR_FLASHLOAD_SUCCESS 0
#define ERROR_OPENFILEIDX_DIR -1
#define ERROR_OPENFILEIDX_NOEXIST -2
#define ERROR_OPENFILEIDX_SUCCESS 1

// Status
#define STATUS_INITALIZED 1

// Cmd Response
#define CMDRESP_BAD_FCNCODE 2 
#define CMDRESP_BAD_APID 3 
#define CMDRESP_NOT_CMD 4
#define CMDRESP_BAD_CHKSUM 5

#if MAX_QUEUE_CMD_LEN > MAX_CMD_LEN
  #error "MAX_QUEUE_CMD_LEN should not be greater than MAX_CMD_LEN"
#endif

/* Define Datatypes */
typedef struct CCSDS_Cmd_t {
  uint32_t timestamp;
  uint8_t bytes[MAX_QUEUE_CMD_LEN];
}CCSDS_Cmd_t;

typedef struct Cmd_Pkt_Buff_t {
  uint16_t buf_size;
  uint16_t end_pos;
  uint8_t cycles_since_last_read;
  uint8_t bytes[MAX_CMD_LEN];
}Cmd_Pkt_Buff_t;

#endif

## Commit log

2017-02-03 mcu block
    [starduino.sch]
2017-02-03 updated libraries and power input
    [starduino.sch]
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2017-02-10 Added Mechanical Drawings
    [AM0820 Stepper.ipt, Arduino Mega.ipt, Arduino Mount.ipt, Arduino and Pi assembly.iam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]
2017-02-11 Added real time clock, edited UART header to include common ground line.
    [starduino.sch]
2017-02-11 Finished adding sensors
    [starduino.sch]
2017-02-12 Finished my part - added IMU, Micro SD, Onboard Flash.
    [starduino.sch]
2017-02-12 aesthetic and spacing for schematic
    [starduino.sch]
2017-02-14 added LED driver, second UART line
    [starduino.sch]
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2017-02-16 Added enable line to LED driver
    [starduino.sch]
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2017-02-16 Removed Hacked Motor PWM Driver/Multiplexer
    Removed hacked motor PWM driver/multiplexer
    [starduino.sch]
2017-02-17 updated CAD for new footprint
    [95947A005_ALUM FEM THRDED HEX STANDOFF.ipt, Antenna.0002.ipt, Antenna.ipt, Arduino Mega.ipt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]
2017-02-18 Added sensor carrier board schematic
    [External_Sensor_Board.sch]
2017-02-18 Finished sensor board layout. Please check.
    [External_Sensor_Board.brd, External_Sensor_Board.sch]
2017-02-19 Added Multiplexer
    Added multiplexer for motor driver and assosciated level-shifting
    circuitry.
    [starduino.sch]
2017-02-19 Renumbered Resistors
    Renumbered resistors in motor driver and multiplexer blocks to maintain
    consecutive numbering.
    [starduino.sch]
2017-02-19 Did a bunch of stuff: Swapped to larger onboard flash (128 MB), Added debug UART, Removed pressure senaor and replaced with header to external board, moved each comm interface to use only one SERCOM.
    [starduino.sch]
2017-02-20 Updated Motor Driver Configuration
    Made motor driver decay mode configurable via the multiplexer
    Changed current sense resistors to 1.05 ohm for more granular control
    over current limiting
    Added a pull-up on nENBL so the output stage will be disabled until
    explicitly commanded otherwise
    Renumbered resistors accordingly
    [starduino.sch]
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2017-02-21 Fixed dumb mistake on external sensor board, screw holes are now right distance apart. Rerouted around hole placement and verfied that DRC was still okay.
    [External_Sensor_Board.brd]
2017-02-22 added gitignore, updated schematic for analog reference and LED driver PWM
    [starduino.sch]
2017-02-22 Finalish CAD for STR
    [15pin female connector.0001.ipt, 15pin female connector.0002.ipt, 15pin female connector.ipt, 15pin male connector.0001.ipt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]
2017-02-22 Renamed some nets, reorganized a bit, removed unnecessary headers
    [starduino.sch]
2017-02-22 Updated Renderings
    [Electronics Box Interior.0001.idw, Electronics Box Interior.idw, Full payload assembly.0003.ipn, Full payload assembly.0004.ipn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]
2017-02-22 Added I2C buffer to STARduino for external board.
    [starduino.sch]
2017-02-22 Added external power switching.
    [starduino.sch]
2017-02-22 Added I2C buffer to external sensor board.
    [External_Sensor_Board.brd, External_Sensor_Board.sch]
2017-02-23 Power supply shit
    [starduino.sch]
2017-02-23 removed bad nets on MCU and removed all greek letters
    [starduino.sch]
2017-02-23 Added J30J connectors
    [starduino.sch]
2017-02-27 Pi things
    [starduino.sch]
2017-02-28 More Pi/Pi CSI things
    [starduino.sch]
2017-02-28 layout file now exists
    [starduino.brd]
2017-02-28 more layout things, MDM adjustments
    [starduino.brd, starduino.sch]
2017-02-28 Altered external sensor board to use J30J-25 connector instead of headers. Board is final aside from logos.
    [External_Sensor_Board.brd, External_Sensor_Board.sch]
2017-03-01 Cleaned up some symbols
    [starduino.brd, starduino.sch]
2017-03-02 Schematic updates
    [starduino.brd, starduino.sch]
2017-03-02 Reorganization and initial shop drawings
    [15pin female connector.ipt, 15pin male connector.ipt, 20mm-box.ipt, 31pin female connector.ipt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]
2017-03-06 Layout and schematic progress
    [starduino.brd, starduino.sch]
2017-03-06 Fixed STEPFREQ schematic bug.
    [starduino.brd, starduino.sch]
2017-03-07 fix stuff
    [starduino.brd]
2017-03-07 Updated Drawings and Solar Sheild
    [1556A650_BRACKET.SLDPRT, 91075A105_18-8 SS MALE-FEM THRDED HEX STANDOFF.SLDPRT, Base Plate Mk 2.0013.ipt, Base Plate Mk 2.0017.ipt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]
2017-03-08 Added bias voltage route to external board
    [External_Sensor_Board.brd, External_Sensor_Board.sch]
2017-03-08 Better differential pair routing.
    [External_Sensor_Board.brd]
2017-03-08 Board routing
    [starduino.brd, starduino.sch]
2017-03-08 Fixed Arduino fuckery
    [starduino.brd, starduino.sch]
2017-03-08 layout stuff
    [starduino.brd, starduino.sch]
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2017-03-09 Began work on pressure sensor library. Realized I specced an inadequate sensor. Specced a better sensor (in the same family). Changed external sensor board to compensate.
    [External_Sensor_Board.brd, External_Sensor_Board.sch]
2017-03-09 Removed unneeded board label.
    [External_Sensor_Board.brd]
2017-03-09 Package stuff
    [starduino.brd, starduino.sch]
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2017-03-10 layout progress
    [starduino.brd, starduino.sch]
2017-03-13 Final layouts and gerbers
    [External_Sensor_Board.brd, External_Sensor_Board.sch, starduino.brd, starduino.sch]
2017-03-13 Added STEP files and updated drawings
    [Base Plate Mk 2.0005.idw, Base Plate Mk 2.0017.ipt, Base Plate Mk 2.0019.ipt, Base Plate Mk 2.idw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]
2017-03-13 Removed Lock Files
    [Heat Block for Pi.0001.idw, Heat Block for Pi.0002.idw, Heat Block for Pi.idw, Tube Holder with camera attachment.0003.idw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]
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2017-03-22 Updated Shop Drawings
    [Base Plate Mk 2.0005.idw, Base Plate Mk 2.0006.idw, Base Plate Mk 2.0019.ipt, Base Plate Mk 2.0020.ipt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]
2017-03-27 Final STARduino stuff+ASM guides
    [starduino.brd]
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2017-03-30 Hole call outs added to some shop drawings
    [Tube Holder Halve 2.0001.idw, Tube Holder Halve 2.0003.idw, Tube Holder Halve 2.0019.ipt, Tube Holder Halve 2.0020.ipt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]
2017-03-30 Hole call outs added to more shop drawings
    [Slide rod connector.0004.idw, Slide rod connector.0005.idw, Slide rod connector.idw, slide rod.0003.idw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]
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2017-04-27 Updated CAD to adjust for CTU Modifications
    [Base Plate Mk 2.0022.ipt, Base Plate Mk 2.0026.ipt, Base Plate Mk 2.ipt, Base Plate Mk 3.0001.ipt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]
2017-05-22 Minor changes to CAD drawings
    [0.25 Standoff.ipt, 18650_thmjpr.ipt, Antenna.ipt, Base Plate Mk 2.0026.ipt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]
2017-05-23 Adjusted some STARduino things
    [starduino.brd, starduino.sch]
2017-05-24 Multiplexer Pinout Change
    Small change to multiplexer layout for increased sense-making.
    [starduino.brd, starduino.sch]
2017-05-24 Beginning rework of expternal sensor board.
    [External_Sensor_Board.brd, External_Sensor_Board.sch]
2017-05-25 Finished External Sensor Board reroute.
    [External_Sensor_Board.brd]
2017-05-26 Minor changes to external board upon review.
    [External_Sensor_Board.brd, External_Sensor_Board.sch]
2017-05-26 Updated Bolt Holes on RSX Deck
    [Base Plate Mk 2.0035.ipt, Base Plate Mk 2.0036.ipt, Base Plate Mk 2.ipt, Bolts go here.0010.idw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]
2017-05-26 Updtaed STEP Files and Shop Drawings for RSX Deck and Slide Rods
    [Base Plate Mk 3.ipt, Full payload assembly mk 2.0048.iam, Full payload assembly mk 2.0049.iam, Full payload assembly mk 2.iam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]
2017-05-26 STARduino progress. De-stupified 28V bias
    [Electronics Box_stp.prt, starduino.brd, starduino.sch]
2017-05-26 Fixed SERCOMS.
    [starduino.brd, starduino.sch]
2017-05-26 Finished schematic changes
    [starduino.brd, starduino.sch]
2017-05-27 New starduino routing done
    [starduino.brd, starduino.sch]
2017-05-27 Change layout version number
    [starduino.brd, starduino.sch]
2017-05-27 Added debug breakout schematic
    [Debug_Breakout.sch]
2017-05-27 Fixed STARduino DRC
    [starduino.brd]
2017-05-27 begin routing debug board.
    [Debug_Breakout.brd]
2017-05-27 Finished STAR debug board.
    [Debug_Breakout.brd, Debug_Breakout.sch]
2017-05-28 Motor holder change and resulting bolt changes
    [Base Plate Mk 2.0008.idw, Base Plate Mk 2.0009.idw, Base Plate Mk 2.0036.ipt, Base Plate Mk 2.0038.ipt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]
2017-05-28 Base plate shop drawing changes
    [Base Plate Mk 2.0009.idw, Base Plate Mk 2.0011.idw, Base Plate Mk 2.0038.ipt, Base Plate Mk 2.0039.ipt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]
2017-05-28 pi camera mount fix
    [Pi cCam Mount.0029.ipt, Pi cCam Mount.ipt]
2017-05-29 Solar Sheild Changes and Tube holder bolt adjustments
    [1556A410_BRACKET.0002.ipt, 1556A410_BRACKET.ipt, 94518A210_MIL SPEC FLAT-HEAD SOCKET CAP SCREW.ipt, 98019A314_MIL SPEC. 300 SERIES SS FLAT WASHER.ipt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]
2017-05-29 STARduino minor mechanical adjustments
    [RSX Deck_stp.prt, starduino.brd]
2017-05-29 ESB traces and breakout 15 pin labels
    [Debug_Breakout.brd, External_Sensor_Board.brd]
2017-05-30 CTU RSX plate step file and shop drawing
    [Debug_Breakout.GBL, Debug_Breakout.GBO, Debug_Breakout.GBP, Debug_Breakout.GBS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]
2017-06-01 STARduino solder paste adjustments
    [RockSat-X Deck Plate 2017 HERMES and STAR Bolt Pattern_stp.prt, starduino.brd, starduino.sch]
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

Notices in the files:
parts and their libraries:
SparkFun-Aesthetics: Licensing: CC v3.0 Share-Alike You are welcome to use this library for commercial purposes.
